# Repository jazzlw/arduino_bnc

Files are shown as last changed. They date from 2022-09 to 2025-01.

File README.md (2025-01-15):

# BNC Shield for Arduino

<!-- ![Image of BNC Shield for Arduino](docs/figs/arduino_bnc.jpg) -->
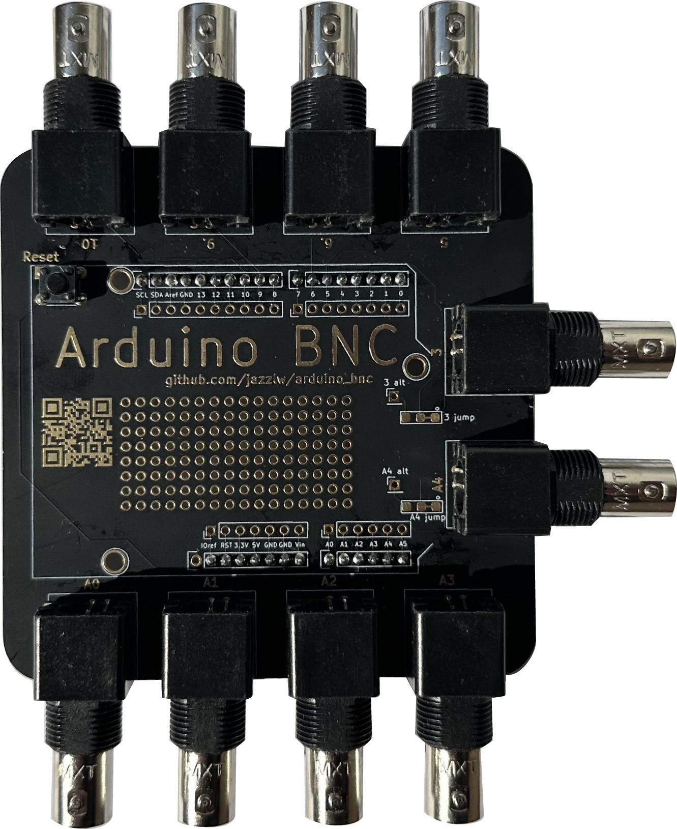
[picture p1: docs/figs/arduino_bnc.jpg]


*Now orderable from my [Etsy store](https://www.etsy.com/listing/1844833694/bnc-shield-for-arduino)*

The BNC Shield for Arduino is a very simple way to reliably connect an Arduino to one or more BNC
cables.

Especially in science, it is very common to use an Arduino to trigger a camera or behavioral system or LED from a computer, and most of the commercially available devices that are triggered have BNC input connections. This often leads to flaky and problematic ways of connecting the Arduino to the BNC cable, and thus experimental setups that are delicate.  This simple shield aims to address this problem and give a reliable solution, without any complicated parts or difficult soldering.

## Features

Up to ten BNC ports attached to different pins on the Arduino.  Five of these pins (3, 5, 6, 9, 10) can be used for digital input our output, and all are PWM capable.  The other five (A0 - A4) can be used for reading analog input voltages, as well as also being usable for digital IO.

There is also a prototyping area with 0.1 inch pitch through holes, in case you want to add any extra parts such as sensors or digital to analog  converters (DACs) or similar. Two of the BNC ports (3 and A4) have jumpers so that they can be easily attached to something in the prototyping area, such as a DAC, instead of to their Arduino pins. See [adding an analog voltage output](docs/adding_analog_out.md) for details and instructions.

## Getting one

To make it super easy to get one of these, I've just put some up on an [Etsy store](https://www.etsy.com/listing/1526648413/arduino-bnc-shield).  You can get just the board, made matte black with high quality immersion gold coating, as shown in the pictures above. You can also get the other parts there, and you can also order it pre-soldered if you want.

With a little more effort, the BNC Shield for Arduino can be ordered easily and cheaply from any PCB board house (such as [pcbway](pcbway.com), [jlcpcb](jlcpcb.com), etc)  using the zipped gerber files in `bnc_shield_pcb/bnc_shield_gerbers.zip`. You'll need to input the size of the desired board, which is 3.6 inches by 3.6 inches. Many board houses have a deal for 5 PCBs of this size for under $10 plus shipping (although without the black solder mask or gold coating mentioned above). The only other parts you need are an Arduino Uno, some BNC jacks, and some header to connect the shield to the Arduino. The whole thing can then be easily and quickly assembled even by someone with no soldering experience using only a soldering iron and solder.

## Build Instructions

The BNC Shield for Arduino was designed to be super easy and quick to assemble, even without any experience! For most use cases, all you need to do is solder some [0.1 inch male header](https://www.digikey.com/en/products/detail/sullins-connector-solutions/PRPC040SAAN-RC/2775214) onto the shield to connect it to the Arduino, and some [BNC Jacks](https://www.digikey.com/en/products/detail/sullins-connector-solutions/PRPC040SAAN-RC/2775214) to connect your BNC cables. For the header, it can be helpful to start by putting the long side of the headers into an Arduino to hold them, and then putting the shield on top to solder it. If you've never soldered before, don't worry, it's very learnable! There are many great YouTube videos and other guides on the internet to show you how, such as [this one from AdaFruit.](https://learn.adafruit.com/adafruit-guide-excellent-soldering/preparation)

Now you're ready to load some code on the Arduino with the [Arduino IDE](https://www.arduino.cc/en/software) and try it out! Check out the things in the `examples` folder for ideas.

## Case
<!-- ![Image of BNC Shield for Arduino](docs/figs/arduino_bnc.jpg) -->
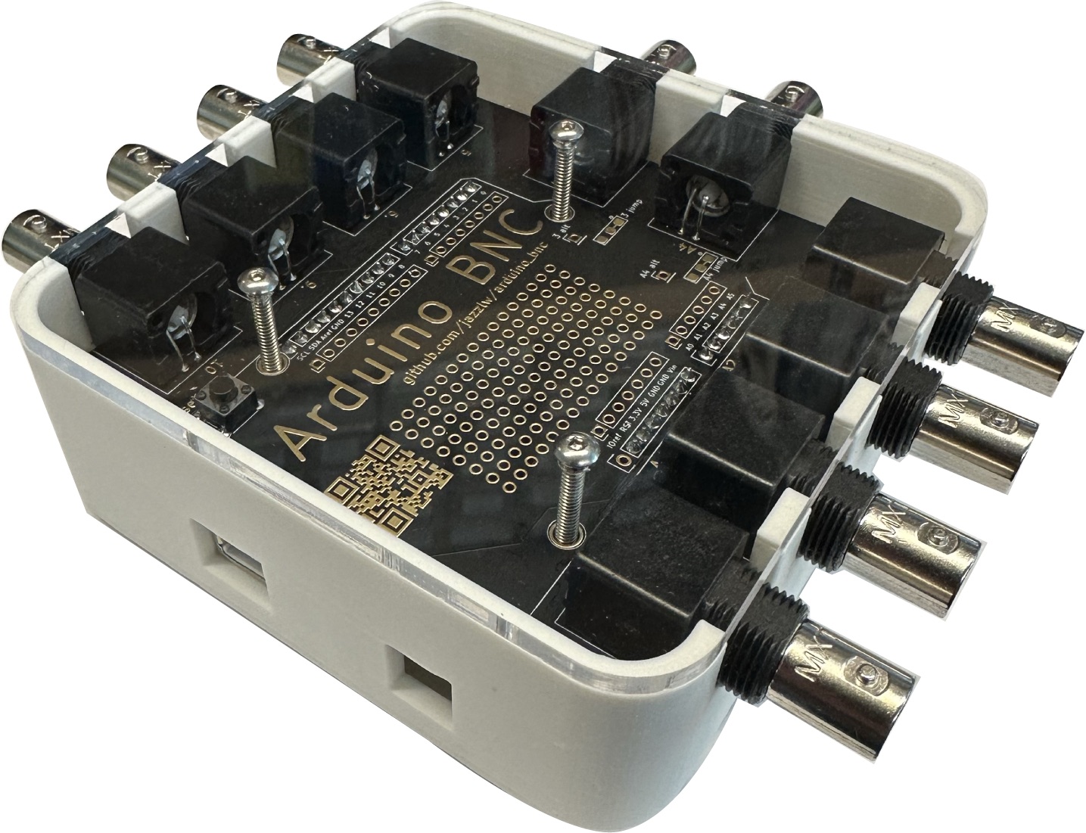
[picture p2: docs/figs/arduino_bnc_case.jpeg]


There are files for a 3D printed case that fits an Arduino Uno with the BNC Shield for Arduino in the folder [arduino_bnc_case](arduino_bnc_case).  You can either print the top lid using the `.stl` file, or laser cut one out of 1/8 inch acrylic using the `.svg` file, as shown to the right. Tap the three standoffs in the bottom of the case to #4-40 using a [tap](https://www.mcmaster.com/25995A125/), and use [1.5 inch long #4-40 screws](https://www.mcmaster.com/92949A120/) to attach the lid and hold the Arduino BNC down.

## Getting one

To make it super easy to get one of these, I've just put some up on an [Etsy store](https://www.etsy.com/listing/1526648413/arduino-bnc-shield).  You can get just the board, made matte black with high quality immersion gold coating, as shown in the pictures above. You can also get the other parts there, and you can order it pre-soldered if you want.

The BNC Shield for Arduino can be ordered easily and cheaply from any PCB board house (such as [pcbway](pcbway.com), [jlcpcb](jlcpcb.com), etc)  using the zipped gerber files in `bnc_shield_pcb/bnc_shield_gerbers.zip`. You'll need to input the size of the desired board, which is 3.6 inches by 3.6 inches. Many board houses have a deal for 5 PCBs of this size for under $10 plus shipping. The only other parts you need are an Arduino Uno, some BNC jacks, and some header to connect the shield to the Arduino. The whole thing can then be easily and quickly assembled even by someone with no soldering experience using only a soldering iron and solder.

### Required parts

You will need a few parts in order to complete the BNC Shield for Arduino, as shown below. For the BNC Jacks, you don't need to install all 10 if you won't be using all 10 channels, just the ones you plan to use.

|Part|Quantity|Part Number|Supplier Link|
|---|---|---|---|
|BNC Shield for Arduino PCB| 1 | N/A | See above
|Arduino Uno|1|A000066 | <https://www.digikey.com/reference-designs/en/open-source-mcu-platforms/2481>|
|BNC Jack|1-10|0731375003 | <https://www.digikey.com/en/products/detail/molex/0731375003/1465136>|
|Male 0.1 in Header|2|PRPC040SAAN-RC | <https://www.digikey.com/en/products/detail/sullins-connector-solutions/PRPC040SAAN-RC/2775214>

### Optional Parts

|Part|Quantity|Part Number|Supplier Link|
|---|---|---|---|
|Reset Button|1| 450-1650-ND |  <https://www.digikey.com/en/products/detail/te-connectivity-alcoswitch-switches/1825910-6/1632536>|
|Shield Stacking Header|1 set| 85|<https://www.adafruit.com/product/85> |
|[Digital to Analog Converter  (DAC)](docs/adding_analog_out.md) | 1| 935 |  <https://www.adafruit.com/product/935>
|4-40 tap for case | 1 | 25995A125 | <https://www.mcmaster.com/25995A125> |
| 1.5 inch long #4-40 screws for case| 3  | 92949A120 | <https://www.mcmaster.com/92949A120>|

<br />This work is licensed under a <a rel="license" href="http://creativecommons.org/licenses/by-sa/4.0/">Creative Commons Attribution-ShareAlike 4.0 International License</a>.

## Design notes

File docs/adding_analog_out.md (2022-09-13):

# Adding an analog voltage output

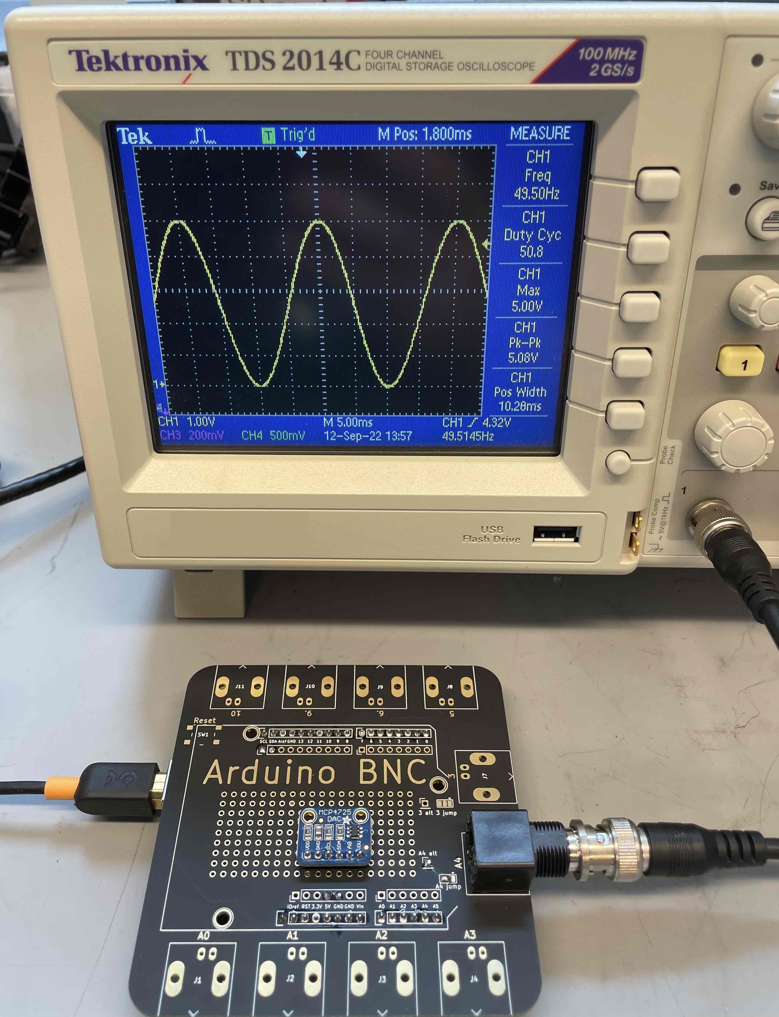
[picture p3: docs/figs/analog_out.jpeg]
Arduino BNC shield with analog out.


The Arduino BNC shied was designed to be simple and easy to use and build, but also to have the ability to be customized and expanded for different use cases.  The prototyping area in the center offers 0.1" through holes for adding parts, and the `A4` and `3` BNC outputs have cuttable jumpers so that they can be attached to something other than their Arduino pins.  One likely use case for these options is adding an analog voltage output.

Arduinos (and many other microcontrollers) have built in options for reading analog voltage inputs (with pins A0-A5), but they can only do digital output. The `analogWrite` function in an Arduino actually outputs a [PWM signal](https://www.wikiwand.com/en/Pulse-width_modulation) on the given pin. If you need an actual analog voltage out, you will need a [digital to analog converter](https://www.wikiwand.com/en/Digital_to_analog_converter) (DAC).  There are many different types of DAC available with different strengths, weaknesses, and communication methods. Here, we'll be using the [MCP4725 DAC board](https://www.adafruit.com/product/935) from Adafruit. [They have written a great guide](https://learn.adafruit.com/mcp4725-12-bit-dac-tutorial) that explains how to use it and has example code and lots more.

### Adding the DAC to the Shield
To add the DAC to the shield, first we need to change BNC `A4` or `3` (here A4, but you can use either) to attach to the alt pin instead of their Arduino Pin.  Do this by cutting the trace connecting the right pad to the middle one, as shown below.  You can do this by scraping with an exacto or other knife blade.  Check the continuity with a multimeter afterwards to make sure that they are no longer connected. Now use a small blob of solder to connect the left pad to the middle, as shown below.  Now the `A4` BNC is connected to the hole labeled `A4 alt` on the board, as you can verify with a multimeter.

<p align="center">
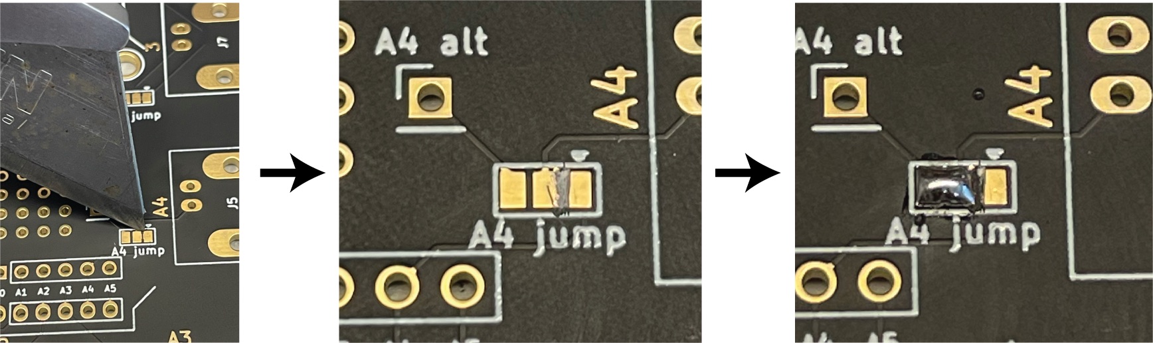
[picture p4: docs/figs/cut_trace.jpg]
Cut the trace and solder the jumper.

</p>

Arduino BNC shield with analog out.

To attach the DAC to the Arduino BNC Shield, solder some 0.1" header to the DAC board and then into the prototyping area somewhere convenient. Then connect the DAC to the matching pins on the shield as shown below. The output of the DAC is connected to the `A4 alt` point and thus to the `A4` BNC.

|DAC Board pin | BNC Shield Pin |Wire color in picture|
|---|---|---|
|Vin / VDD | 5V  | Red
|GND | GND | Black
|SCL | SCL | Yellow
|SDA | SDA | Blue (long)
Vout | A4 alt| Blue (short)

## Using it!
Now you're ready to have analog voltage output!  Download the [Adafruit library for the MCP4725](https://github.com/adafruit/Adafruit_MCP4725) from their github or using the library manager in the Arduino IDE, and load one of their examples onto the Arduino to try it out!

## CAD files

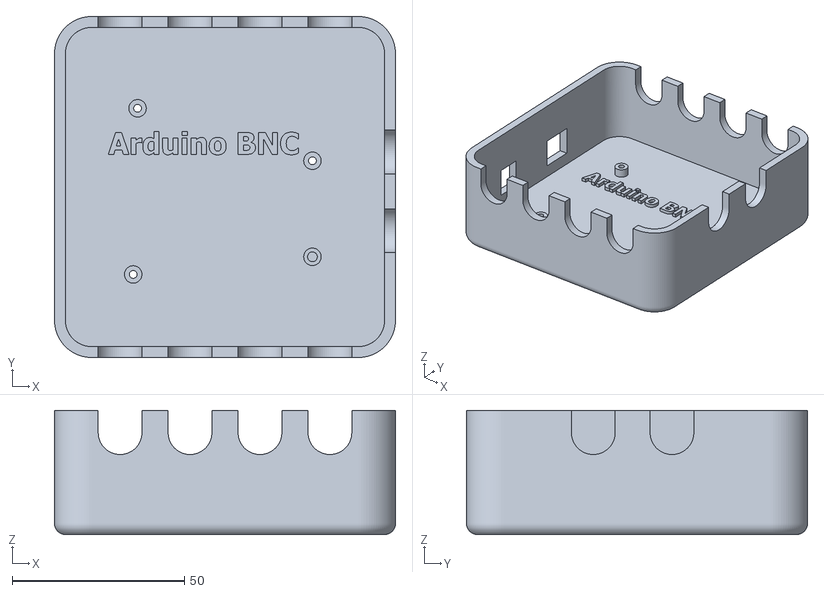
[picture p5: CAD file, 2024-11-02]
arduino_bnc_case/arduino_bnc_case_bottom.stl
99.1 x 99.1 x 36.0

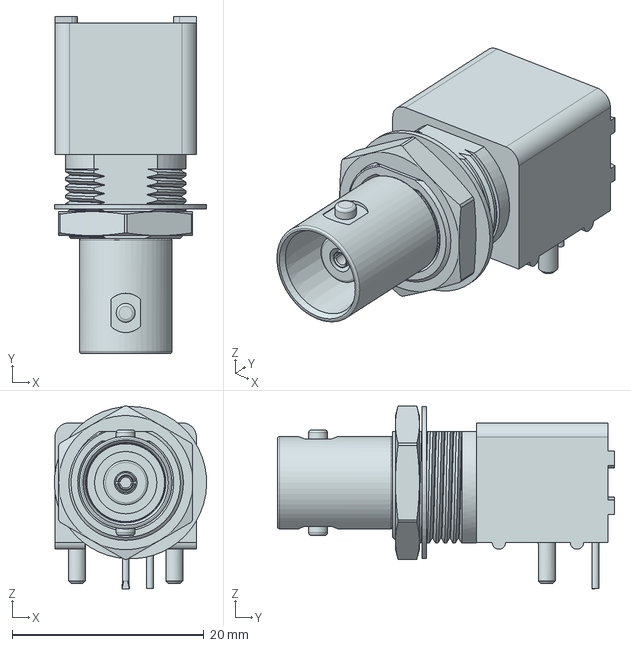
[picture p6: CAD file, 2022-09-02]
bnc_shield_pcb/BNC_connector.stp
15.9 x 35.2 x 19.1 mm

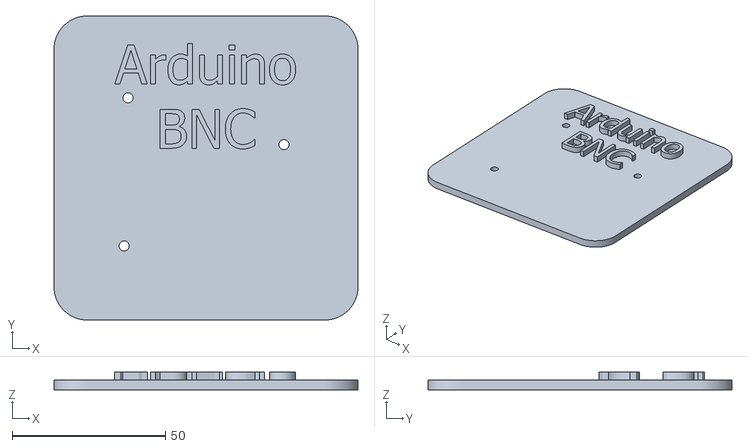
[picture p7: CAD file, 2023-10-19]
arduino_bnc_case/arduino_bnc_case_top.stl
99.1 x 99.1 x 5.72

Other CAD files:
arduino_bnc_case/arduino_bnc_case_bottom.ipt

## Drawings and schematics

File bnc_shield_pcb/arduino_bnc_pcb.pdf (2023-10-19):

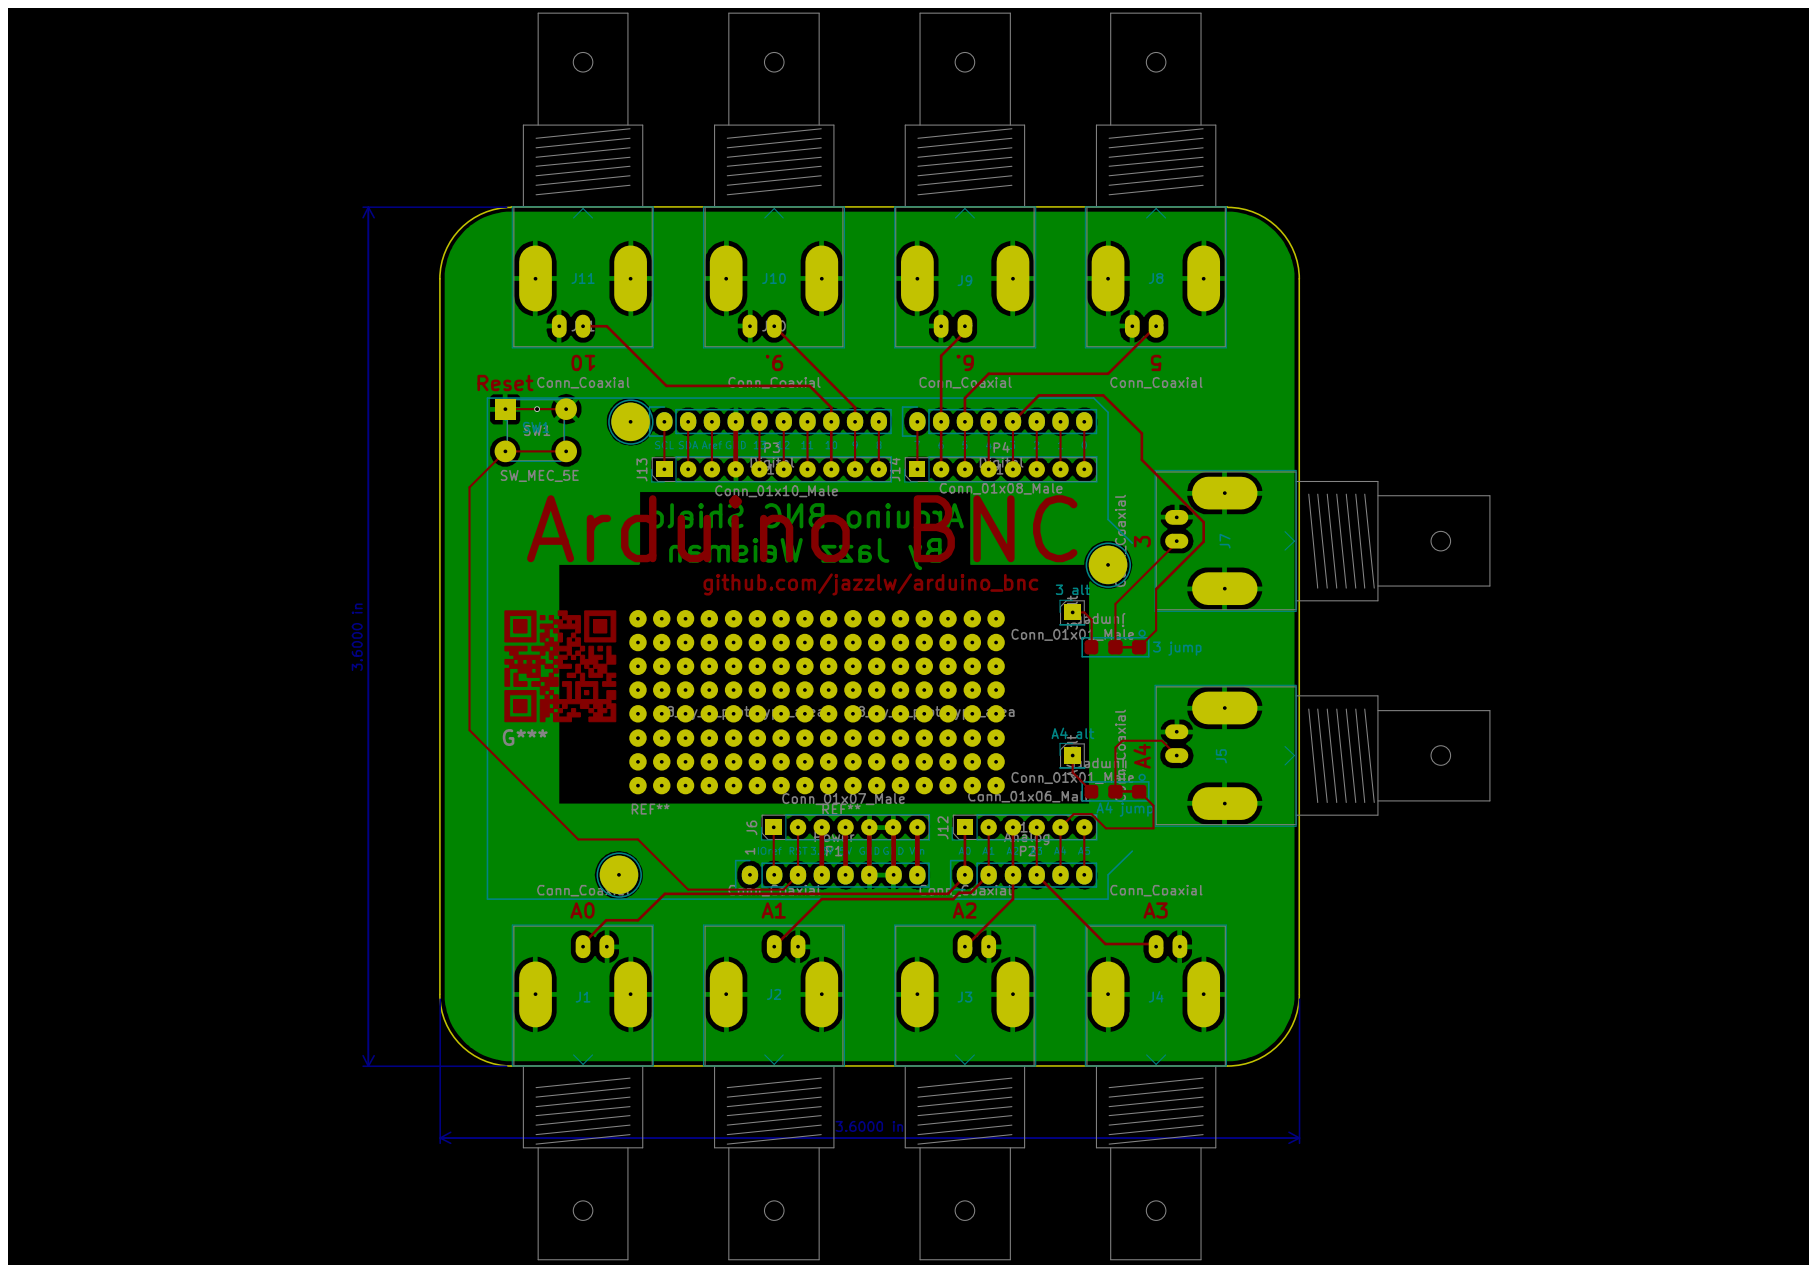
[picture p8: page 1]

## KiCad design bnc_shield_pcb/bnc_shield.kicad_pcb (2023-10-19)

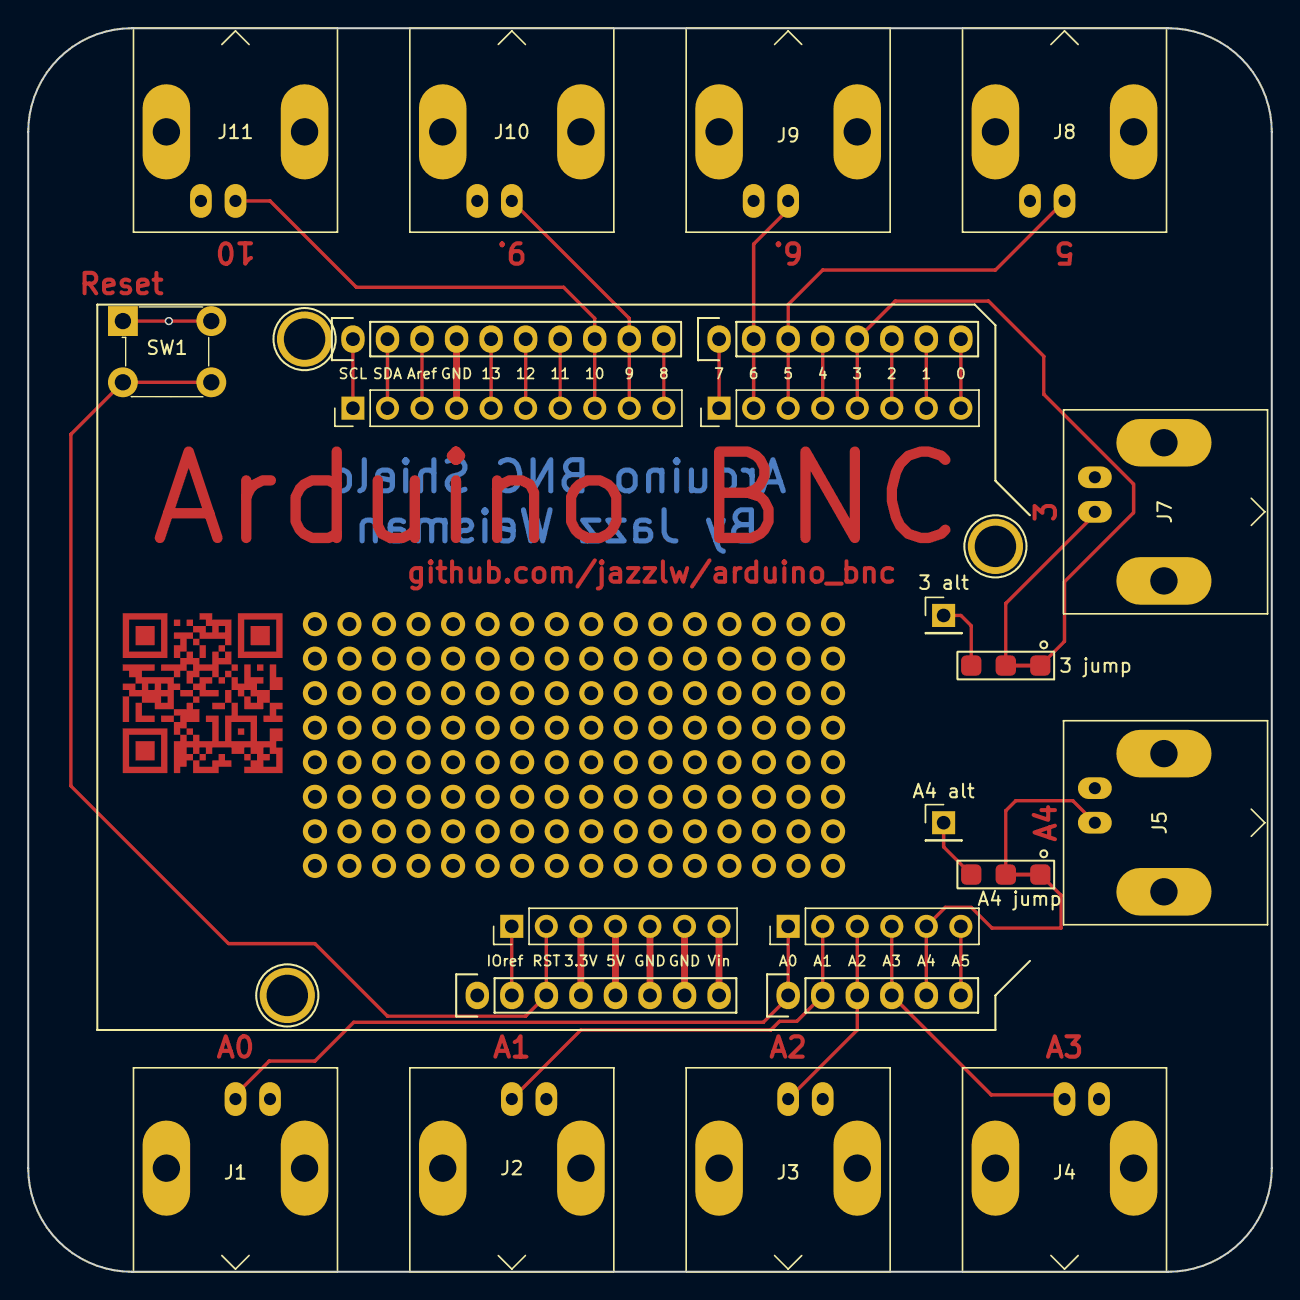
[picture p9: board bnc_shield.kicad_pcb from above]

Board: 2 copper layers, 91.4 x 91.4 mm, 26 parts (0 on the bottom side), 31 nets.

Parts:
3 alt: Conn_01x01_Male; PinHeader_1x01_P2.54mm_Vertical
3 jump: jumper; SolderJumper-3-P2.54mm_Bridged12
A4 alt: Conn_01x01_Male; PinHeader_1x01_P2.54mm_Vertical
A4 jump: jumper; SolderJumper-3-P2.54mm_Bridged12
J1, J2, J3, J4, J5, J7, J8, J9, J10, J11: Conn_Coaxial; BNC_Amphenol_B6252HB-NPP3G-50_Horizontal
J6: Conn_01x07_Male; PinHeader_1x07_P2.54mm_Vertical
J12: Conn_01x06_Male; PinHeader_1x06_P2.54mm_Vertical
J13: Conn_01x10_Male; PinHeader_1x10_P2.54mm_Vertical
J14: Conn_01x08_Male; PinHeader_1x08_P2.54mm_Vertical
P1: Power; Socket_Strip_Arduino_1x08
P2: Analog; Socket_Strip_Arduino_1x06
P3: Digital; Socket_Strip_Arduino_1x10
P4: Digital; Socket_Strip_Arduino_1x08
P5, P7, P8: CONN_01X01; Arduino_1pin
SW1: SW_MEC_5E; Switch_Tactile_THT_6x6mm

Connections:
+3V3: J6.3, P1.4
+5V: J6.4, P1.5
/0(Rx): J14.8, P4.8
/1(Tx): J14.7, P4.7
/2: J14.6, P4.6
/3(**): 3 jump.1 (A), J14.5, P4.5
/4: J14.4, P4.4
/5(**): J8.1 (In), J14.3, P4.3
/6(**): J9.1 (In), J14.2, P4.2
/7: J14.1, P4.1
/8: J13.10, P3.10
/9(**): J10.1 (In), J13.9, P3.9
/10(**/SS): J11.1 (In), J13.8, P3.8
/11(**/MOSI): J13.7, P3.7
/12(MISO): J13.6, P3.6
/13(SCK): J13.5, P3.5
/A0: J1.1 (In), J12.1, P2.1
/A1: J2.1 (In), J12.2, P2.2
/A2: J3.1 (In), J12.3, P2.3
/A3: J4.1 (In), J12.4, P2.4
/A4(SDA): A4 jump.1 (A), J12.5, J13.2, P2.5, P3.2
/A5(SCL): J12.6, J13.1, P2.6, P3.1
/AREF: J13.3, P3.3
/IOREF: J6.1, P1.2
/Reset: J6.2, P1.3, SW1.3 (K), SW1.4 (A)
/Vin: J6.7, P1.8
GND: J1.2 (Ext), J2.2 (Ext), J3.2 (Ext), J4.2 (Ext), J5.2 (Ext), J6.5, J6.6, J7.2 (Ext), J8.2 (Ext), J9.2 (Ext), J10.2 (Ext), J11.2 (Ext), J13.4, P1.6, P1.7, P3.4, SW1.1, SW1.2
unnamed: A4 jump.2 (C), J5.1 (In)
unnamed: 3 jump.2 (C), J7.1 (In)
unnamed: A4 alt.1, A4 jump.3 (B)
unnamed: 3 alt.1, 3 jump.3 (B)

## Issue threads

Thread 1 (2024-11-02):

### ISSUE TITLE
STL file for case bottom

### ISSUE THREAD

**Issue by nikolaskaralis** [jazzlw/arduino_bnc#1]
Hi Jazz,

awesome project! 
I've been meaning to do something like this for years.

The bottom case file is .ipt (Inventor format).
Could you by any chance provide a .stl file?

Thanks in advance!

**Comment by jazzlw** [comment]
Thanks, I'm glad you like it!  And thanks for catching that, it was definitely supposed to be an stl file!  I've fixed it now, let me know if it works of if you have any other questions!

https://github.com/jazzlw/arduino_bnc/commit/d4fa02aca514f6f7a8b0c5207c1f0d6cd495ebae

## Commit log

2022-09-02 Initial Commit. First boards ordered
    [BNC_connector.stp, bnc_shield-B_Cu.gbr, bnc_shield-B_Mask.gbr, bnc_shield-B_Paste.gbr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]
2023-06-13 added board dimensions
    [bnc_shield.kicad_pcb]
2023-07-20 Version 2, as ordered
    [bnc_shield-B_Cu.gbr, bnc_shield-B_Mask.gbr, bnc_shield-B_Paste.gbr, bnc_shield-B_Silkscreen.gbr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]
2023-10-19 updated with case and new version
    [arduino_bnc_case_bottom.ipt, arduino_bnc_case_top.stl, bnc_shield.kicad_pcb]
2024-11-02 added stl of case bottom
    [arduino_bnc_case_bottom.stl]
